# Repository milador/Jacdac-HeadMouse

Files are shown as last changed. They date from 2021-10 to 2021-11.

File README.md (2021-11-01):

# Jacdac-HeadMouse

A headmouse concept based on <a href="https://microsoft.github.io/jacdac-docs/">Jacdac</a> ecosystem. The sample <a href="https://makecode.microbit.org/_heFTpmWCwD0o">Jacdac-HeadMouse test code</a> was used during Microsoft Global Hackathon 2021.

## Main Unit

Top View: 
<p align="center">
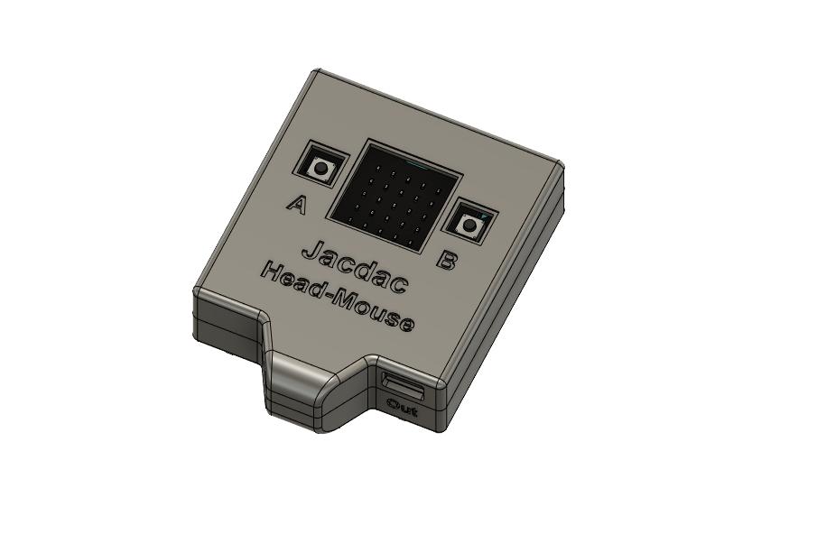
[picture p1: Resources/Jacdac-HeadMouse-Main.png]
Jacdac-HeadMouse Main Top View

</p>

Bottom View:  
<p align="center">
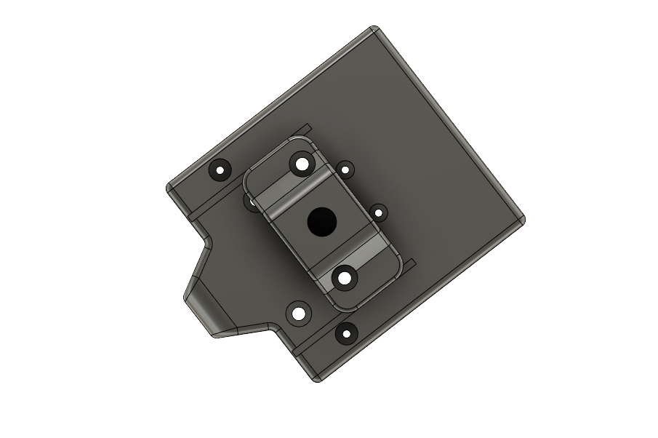
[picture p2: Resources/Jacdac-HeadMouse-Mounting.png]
Jacdac-HeadMouse Bottom View

</p>

Top Removed View:  
<p align="center">
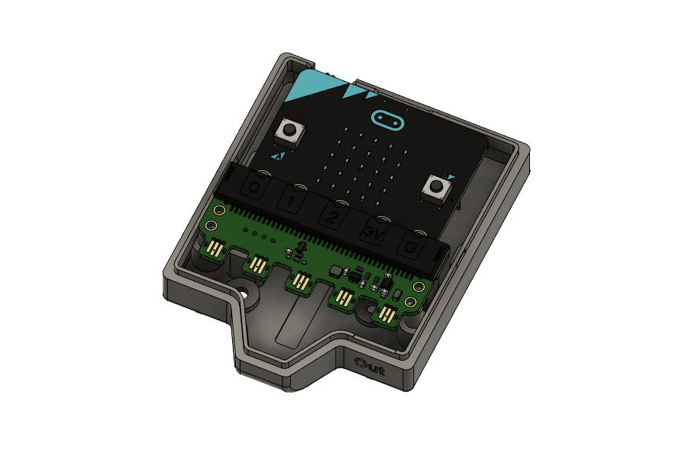
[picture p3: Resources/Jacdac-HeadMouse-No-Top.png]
Jacdac-HeadMouse Top Removed View

</p>

Accelerometer Inserted View:  
<p align="center">
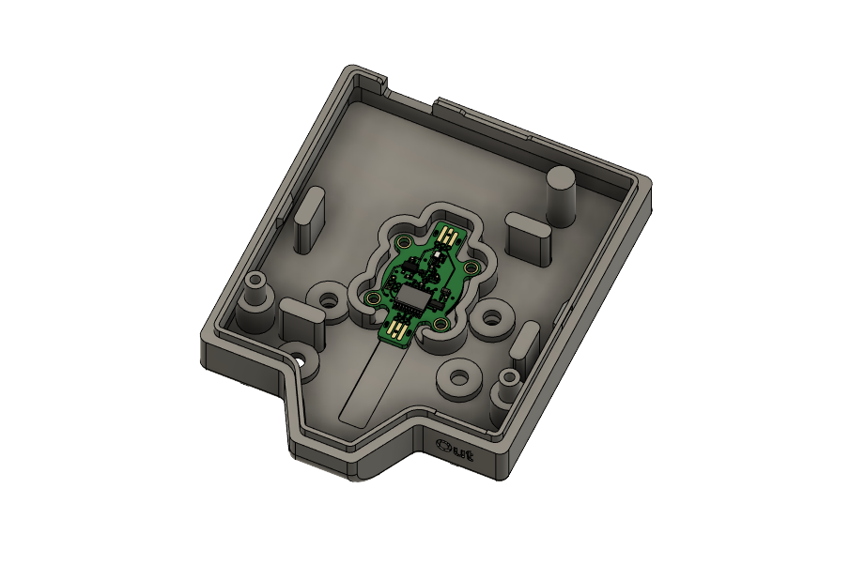
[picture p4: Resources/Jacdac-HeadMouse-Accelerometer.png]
Jacdac-HeadMouse Accelerometer Inserted View

</p>

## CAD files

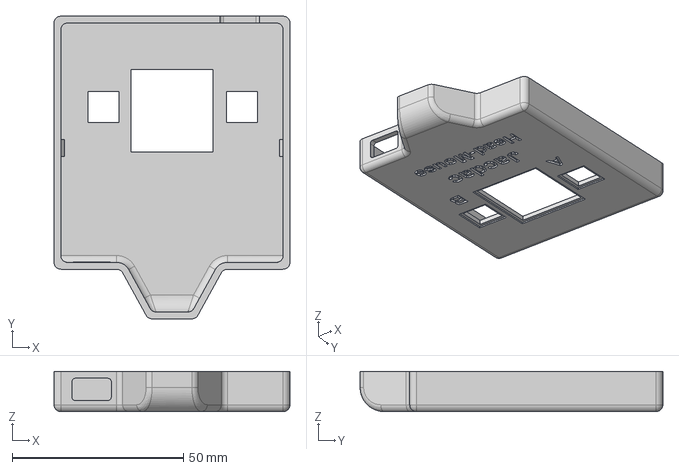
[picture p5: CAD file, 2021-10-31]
Hardware/Enclosure/STEP/Jacdac-HeadMouse-Top.step
69.0 x 88.5 x 11.8 mm

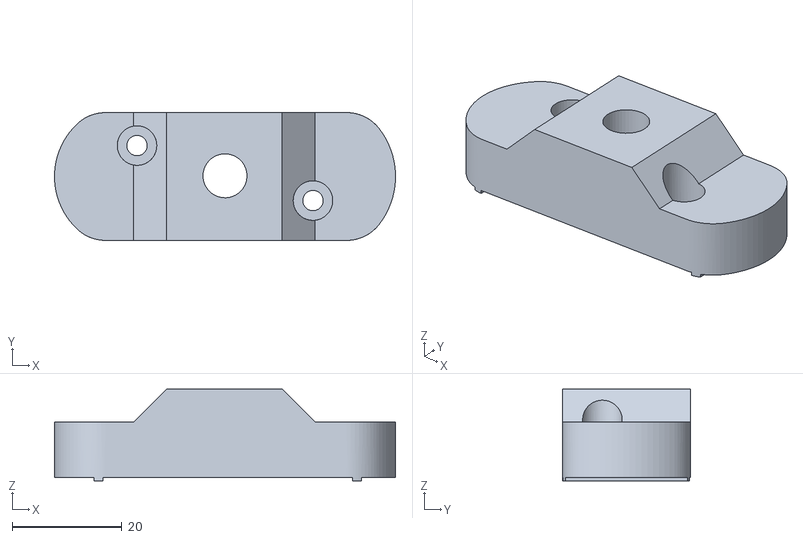
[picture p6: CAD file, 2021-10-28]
Hardware/Enclosure/STL/Jacdac-HeadMouse-Mounting-v1.stl
62.0 x 23.2 x 16.7

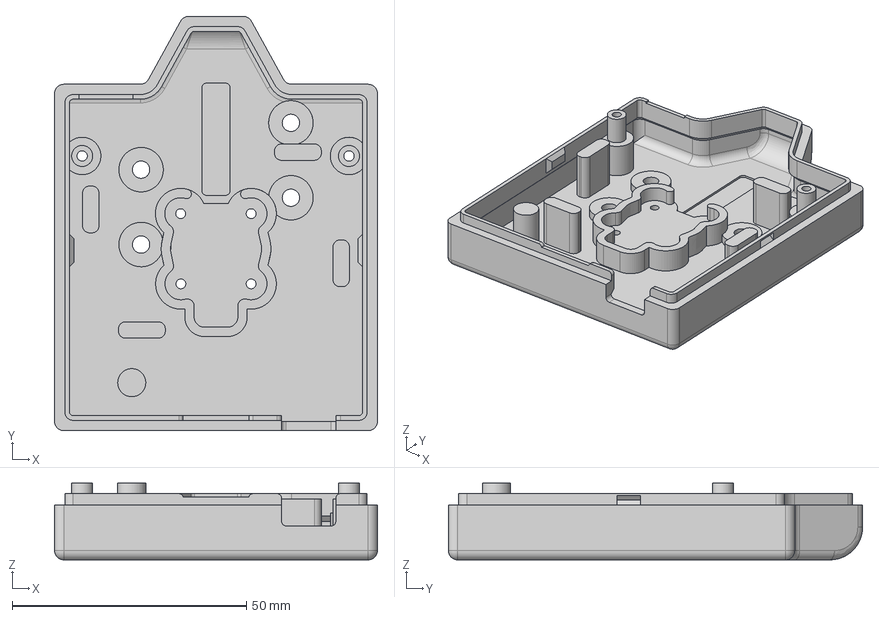
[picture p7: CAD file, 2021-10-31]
Hardware/Enclosure/STEP/Jacdac-HeadMouse-Bottom.step
69.0 x 88.5 x 16.4 mm

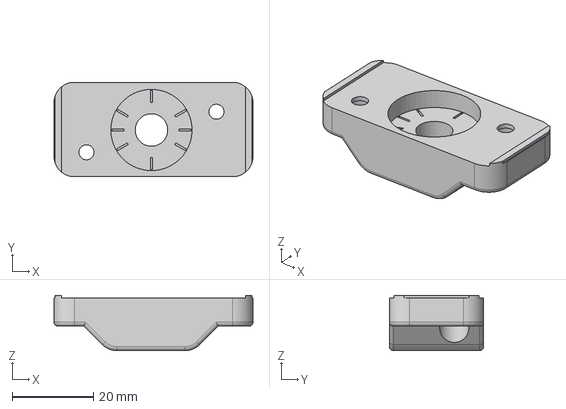
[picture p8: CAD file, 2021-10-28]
Hardware/Enclosure/STEP/Jacdac-HeadMouse-Mounting.step
49.0 x 23.2 x 13.6 mm

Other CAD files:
Hardware/Enclosure/STL/Jacdac-HeadMouse-Bottom.stl
Hardware/Enclosure/STL/Jacdac-HeadMouse-Mounting.stl
Hardware/Enclosure/STL/Jacdac-HeadMouse-Top.stl

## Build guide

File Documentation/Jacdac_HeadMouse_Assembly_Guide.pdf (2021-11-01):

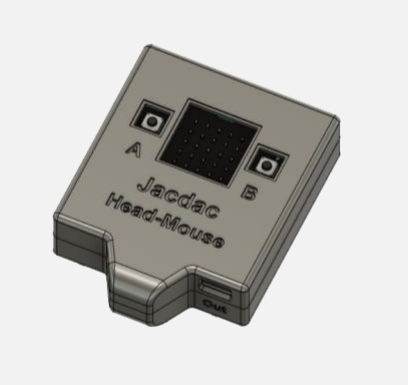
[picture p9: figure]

# JACDAC HEADMOUSE

A head mouse concept based on Jacdac microcontrollers ecosystem.

## Version 1.0

https://github.com/milador/Jacdac-HeadMouse

1

## Contents

Components List | 1
Software | 3
JavaScript Demo Code | 3
Hardware Assembly | 6
Enclosure design | 6
Assembly | 7

## Components List

### 1. MICRO:BIT V2 x 1

2. MICRO:BIT JACDAPTOR (https://microsoft.github.io/jacdac-docs/devices/microbit/foundation/microbitv2) x 1
3. JACDAC ACCELEROMETER MODULE (https://microsoft.github.io/jacdac-docs/devices/microsoft/research/jmaccelerometer30v10) x 1

### 4. JACDAC CABLE x 2

### 5. LITHIUM-ION POLYMER BATTERY- 3.7V 1200MAH (https://www.adafruit.com/product/258) x 1

### 6. M3 HEX NUT x 2

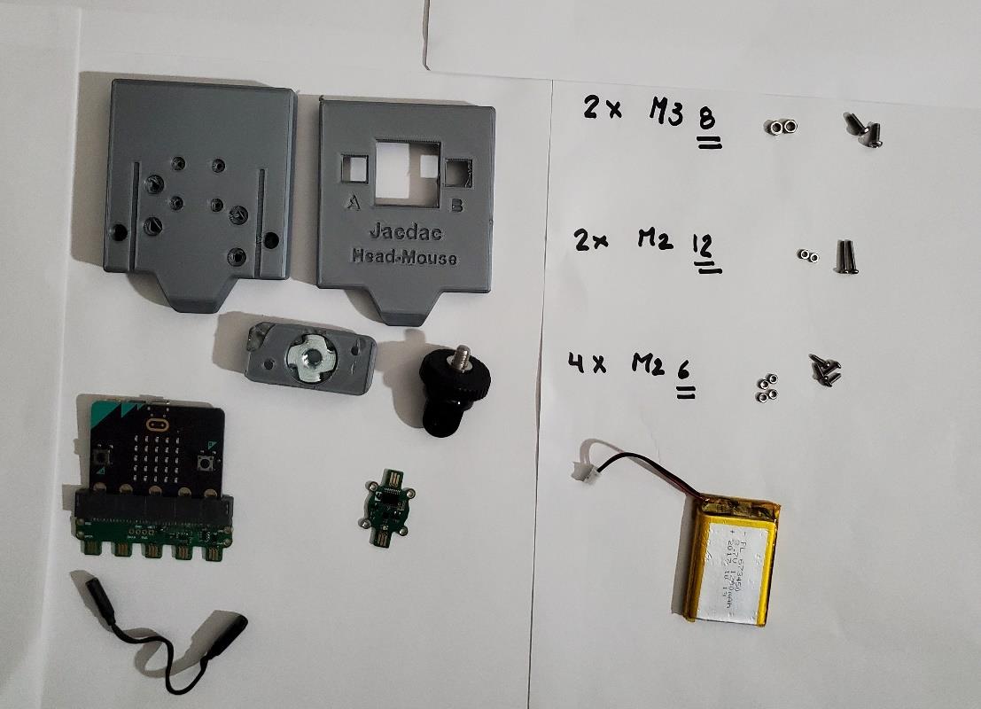
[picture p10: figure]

2

### 7. M3-8MM SCREW x 2

### 8. M2 HEX NUT x 6

### 9. M2-6MM SCREW x 4

### 10. M2-12MM SCREW x 2

11. AMAZON BASICS HEAD STRAP CAMERA MOUNT FOR GOPRO (https://www.amazon.ca/gp/product/B00R4YCKIK/) x 1
12. GOPRO MOUNT TO 1/4-INCH 20 CAMERA ADAPTER (https://www.amazon.ca/gp/product/B00IQ7PRHU) x 1
13. 1/4-INCH 20 TEE NUT x 1
14. (OPTIONAL) JACDAC ACCESS SWITCH OUTPUT MODULE (https://microsoft.github.io/jacdac-docs/devices/microsoft/research/jmaccessswitchoutputv11) x 1
- Item 14 is optional, and it’s only required if you would like to control an access switch instead of

cursor.

3

## Software

The demo code written using MakeCode blocks is available and it can be accessed through following link.

https://makecode.microbit.org/_heFTpmWCwD0o

### JavaScript Demo Code

You can also copy and paste the following code to MakeCode JavaScript code editor field:

input.onButtonPressed(Button.A, function () {

initialize()

})

function initialize () {

counter = 3

while (counter >= 0) {

basic.showNumber(counter)

basic.pause(1000)

counter += -1

}

basic.pause(200)

soundExpression.hello.play()

x_init = modules.accelerometer1.x()

y_init = modules.accelerometer1.z()

}

let y_val = 0

let x_val = 0

let counter = 0

4

let y_init = 0

let x_init = 0

let count = 0

let x_threshold = 0.05

let y_up_threshold = 0.22

let y_down_threshold = 0.05

x_init = -0.2

y_init = 0.1

initialize()

basic.forever(function () {

led.stopAnimation()

if (modules.accelerometer1.x() < x_init - x_threshold) {

x_val = 1

} else if (modules.accelerometer1.x() > x_init + x_threshold) {

x_val = -1

} else {

x_val = 0

}

if (modules.accelerometer1.z() < y_init - y_up_threshold) {

y_val = 1

} else if (modules.accelerometer1.z() > y_init + y_down_threshold) {

y_val = -1

} else {

y_val = 0

}

if (x_val == 0 && y_val == 0) {

basic.showLeds(`

5

`)

modules.hidKeyboard1.clear()

} else if (x_val == 0 && y_val != 0) {

if (y_val > 0) {

basic.showArrow(ArrowNames.North)

modules.hidKeyboard1.key(jacdac.HidKeyboardAction.Press, jacdac.HidKeyboardModifiers.None, jacdac.HidKeyboardKey.UpArrow)

} else {

basic.showArrow(ArrowNames.South)

modules.hidKeyboard1.key(jacdac.HidKeyboardAction.Press, jacdac.HidKeyboardModifiers.None, jacdac.HidKeyboardKey.DownArrow)

}

} else if (x_val != 0 && y_val == 0) {

if (x_val > 0) {

basic.showArrow(ArrowNames.East)

modules.hidKeyboard1.key(jacdac.HidKeyboardAction.Press, jacdac.HidKeyboardModifiers.None, jacdac.HidKeyboardKey.LeftArrow)

} else {

basic.showArrow(ArrowNames.West)

modules.hidKeyboard1.key(jacdac.HidKeyboardAction.Press, jacdac.HidKeyboardModifiers.None, jacdac.HidKeyboardKey.RightArrow)

}

} else if (x_val != 0 && y_val != 0) {

if (x_val > 0 && y_val > 0) {

basic.showArrow(ArrowNames.NorthEast)

} else if (x_val < 0 && y_val > 0) {

basic.showArrow(ArrowNames.NorthWest)

} else if (x_val < 0 && y_val < 0) {

basic.showArrow(ArrowNames.SouthWest)

} else if (x_val < 0 && y_val > 0) {

basic.showArrow(ArrowNames.SouthEast)

6

} else {

}

} else {

}

})

## Hardware Assembly

### Enclosure design

The enclosure/housing files in STL format can be downloaded from GitHub repository under Hardware directory.

https://github.com/milador/Jacdac-HeadMouse/tree/main/Hardware/Enclosure/STL

Please print the following STL files:

- Jacdac-HeadMouse-Top.stl x 1
- Jacdac-HeadMouse-Bottom.stl x 1
- Jacdac-HeadMouse-Mounting.stl x 1

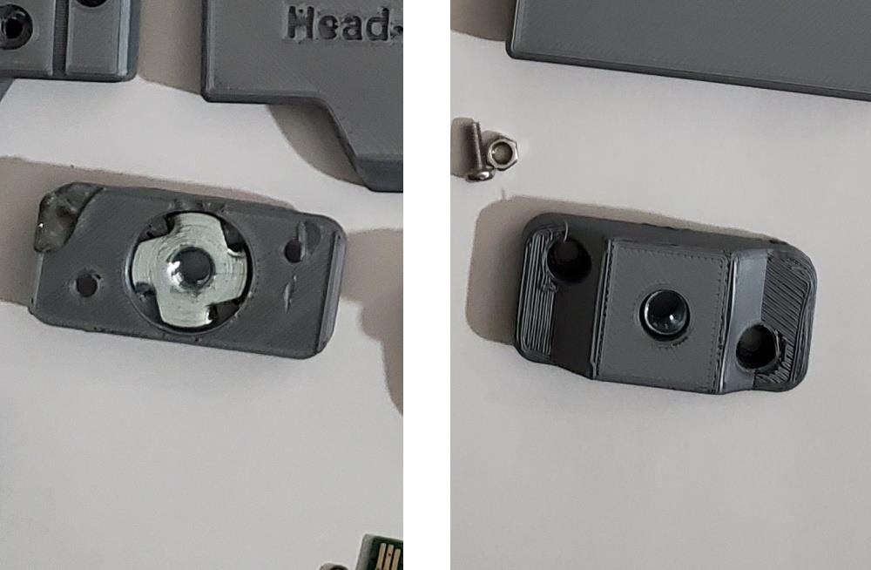
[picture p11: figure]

7

### Assembly

Step 1: Insert the 1/4-inch-20 Tee Nut into the mounting enclosure piece and press it inward using a soldering iron.

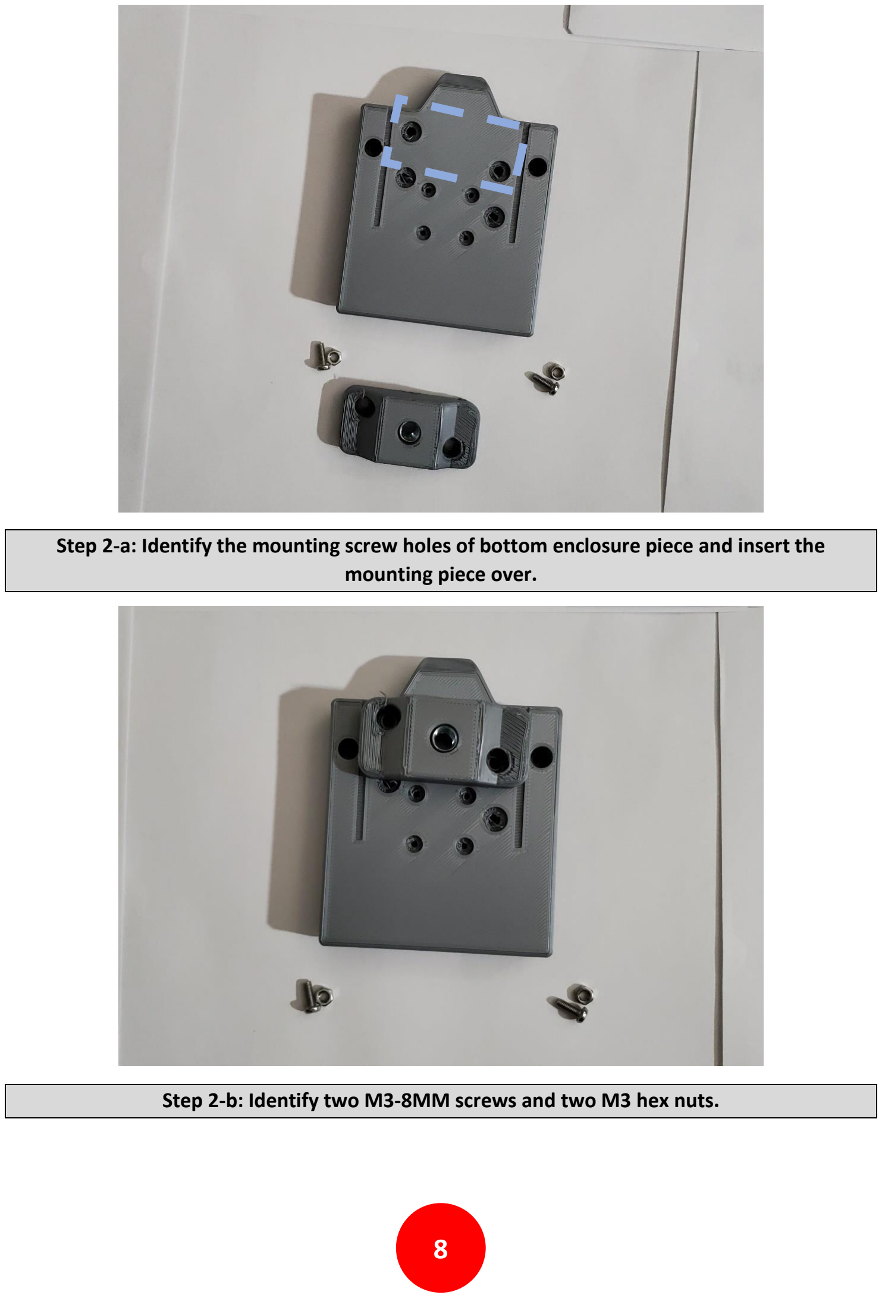
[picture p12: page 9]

8

Step 2-a: Identify the mounting screw holes of bottom enclosure piece and insert the mounting piece over.
Step 2-b: Identify two M3-8MM screws and two M3 hex nuts.

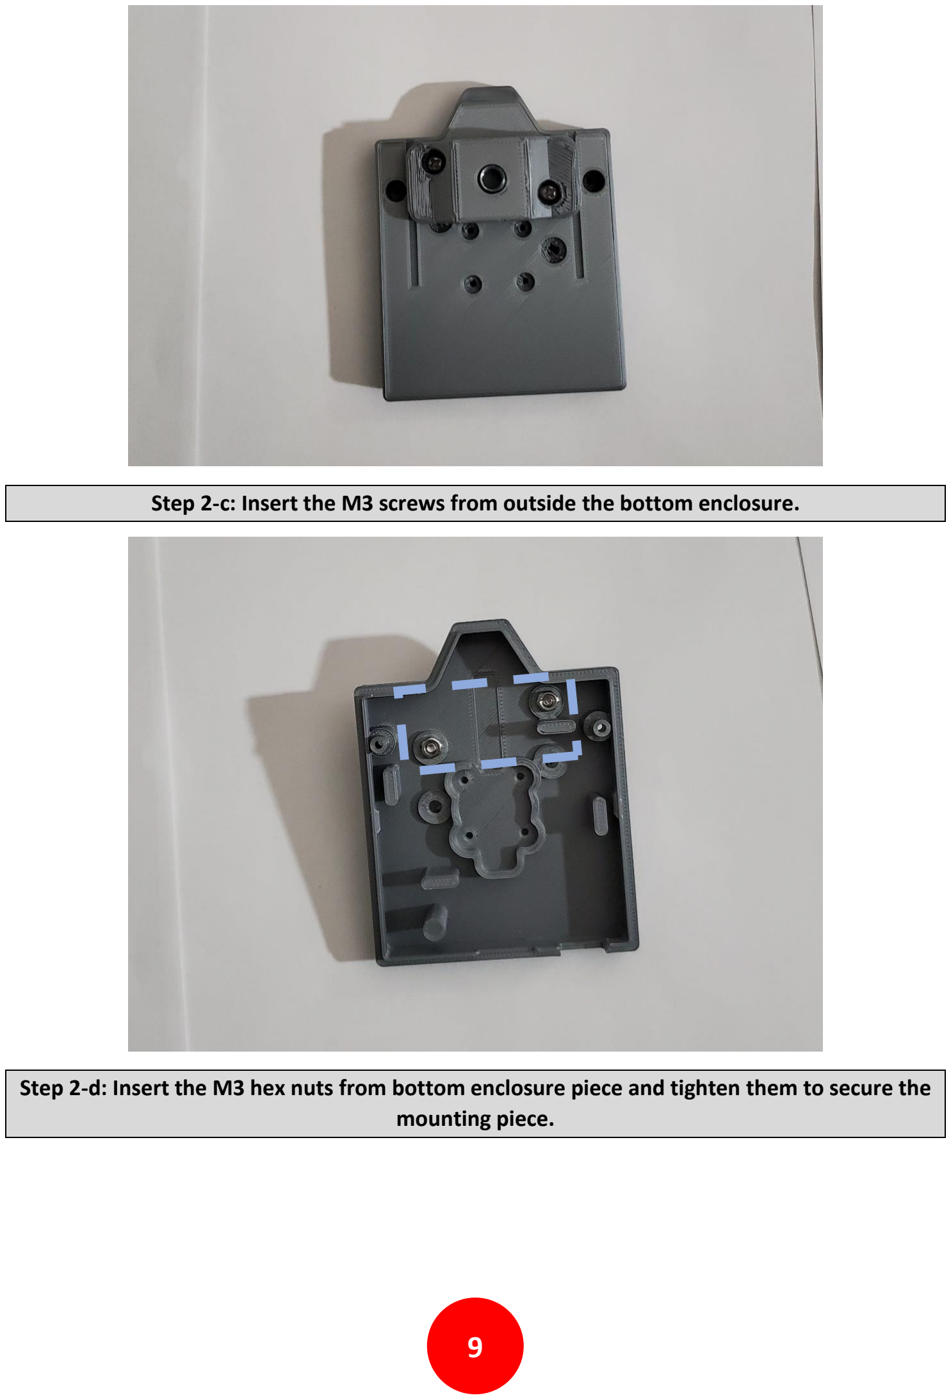
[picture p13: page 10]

9

Step 2-c: Insert the M3 screws from outside the bottom enclosure.
Step 2-d: Insert the M3 hex nuts from bottom enclosure piece and tighten them to secure the mounting piece.

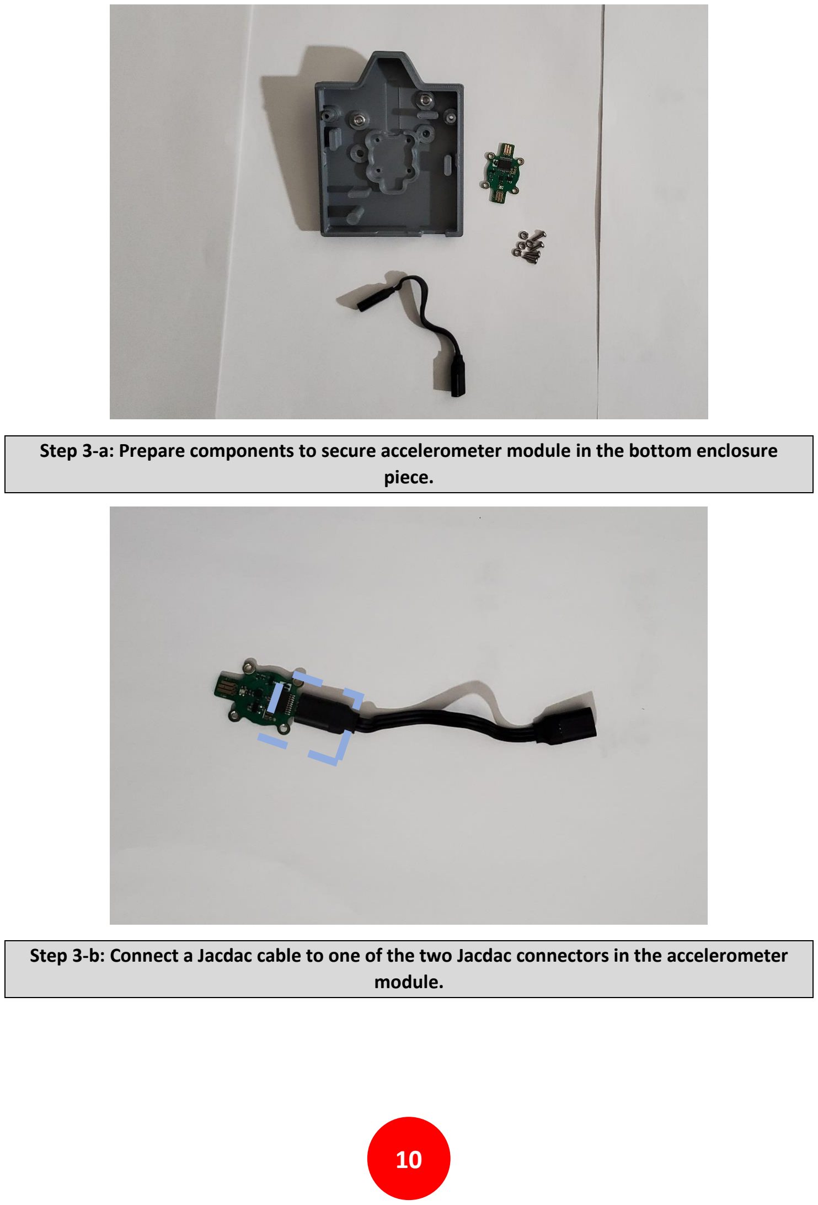
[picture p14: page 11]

10

Step 3-a: Prepare components to secure accelerometer module in the bottom enclosure piece.
Step 3-b: Connect a Jacdac cable to one of the two Jacdac connectors in the accelerometer module.

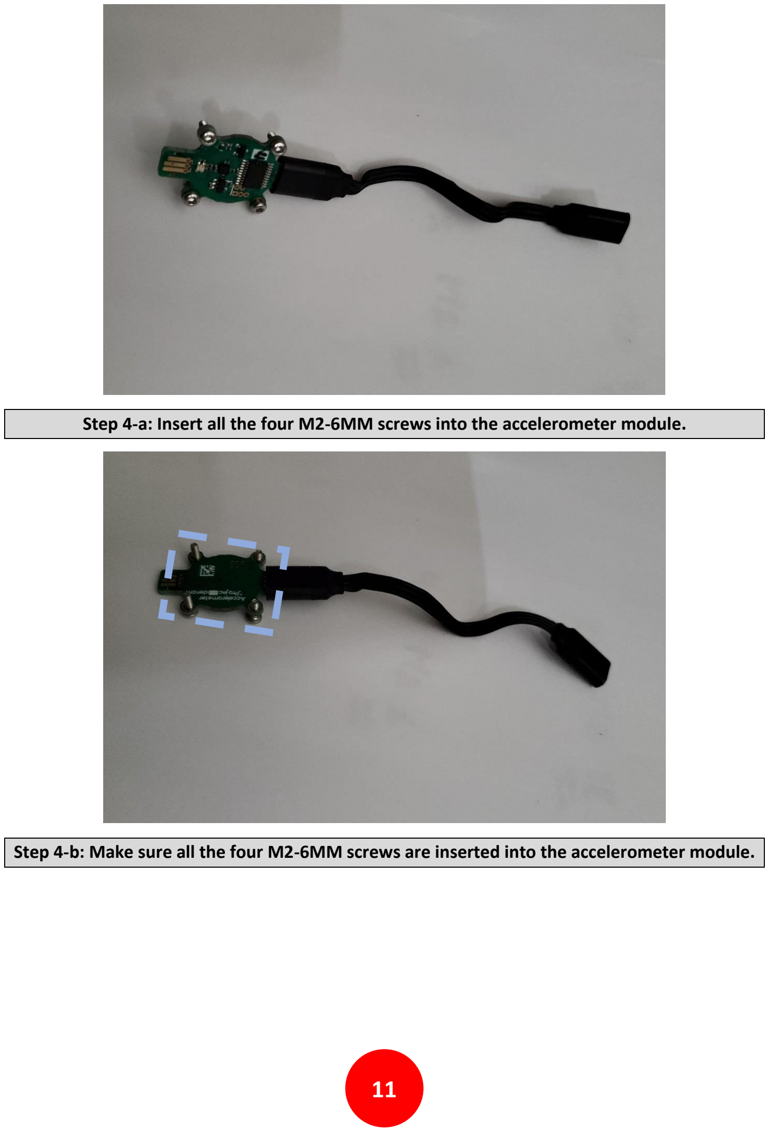
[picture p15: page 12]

11

Step 4-a: Insert all the four M2-6MM screws into the accelerometer module.
Step 4-b: Make sure all the four M2-6MM screws are inserted into the accelerometer module.

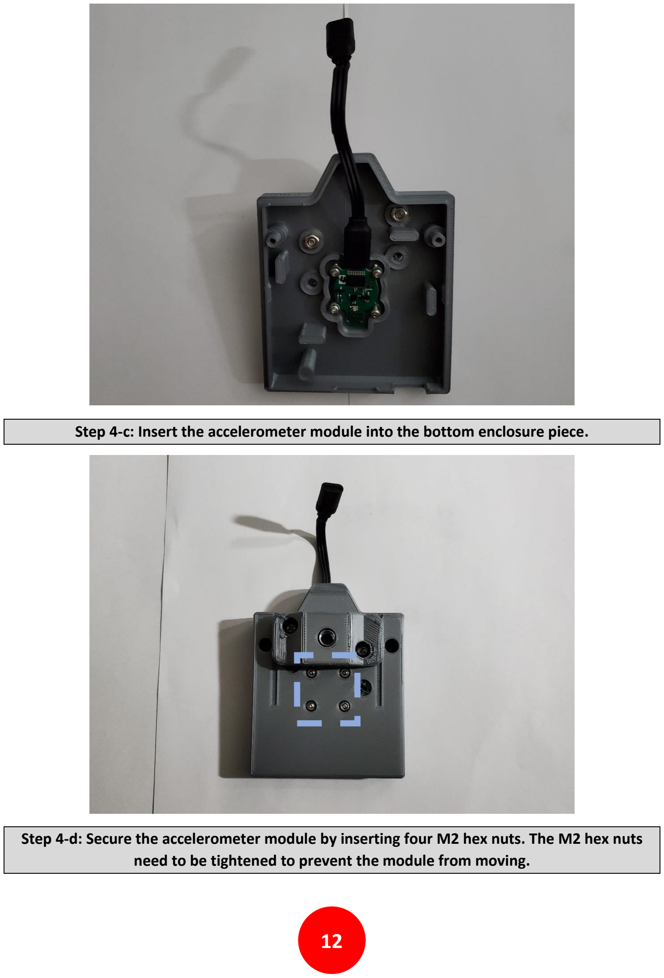
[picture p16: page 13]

12

Step 4-c: Insert the accelerometer module into the bottom enclosure piece.
Step 4-d: Secure the accelerometer module by inserting four M2 hex nuts. The M2 hex nuts need to be tightened to prevent the module from moving.

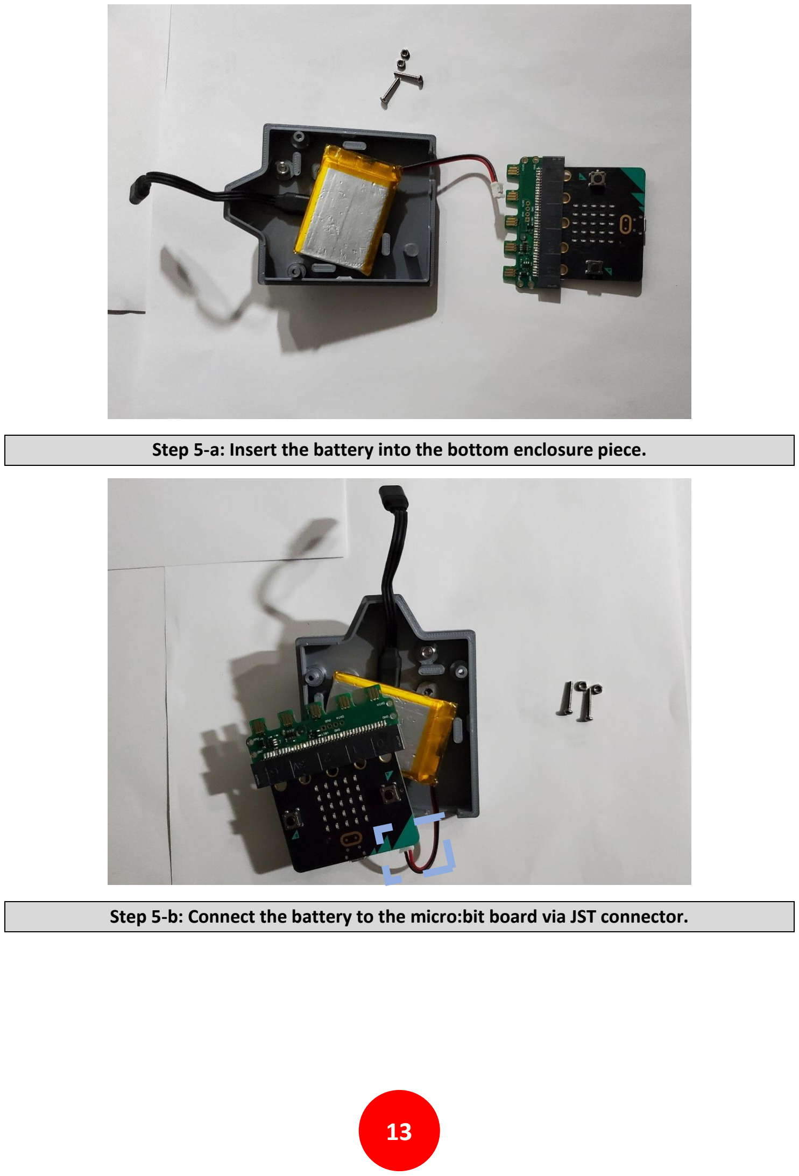
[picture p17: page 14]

13

Step 5-a: Insert the battery into the bottom enclosure piece.
Step 5-b: Connect the battery to the micro:bit board via JST connector.

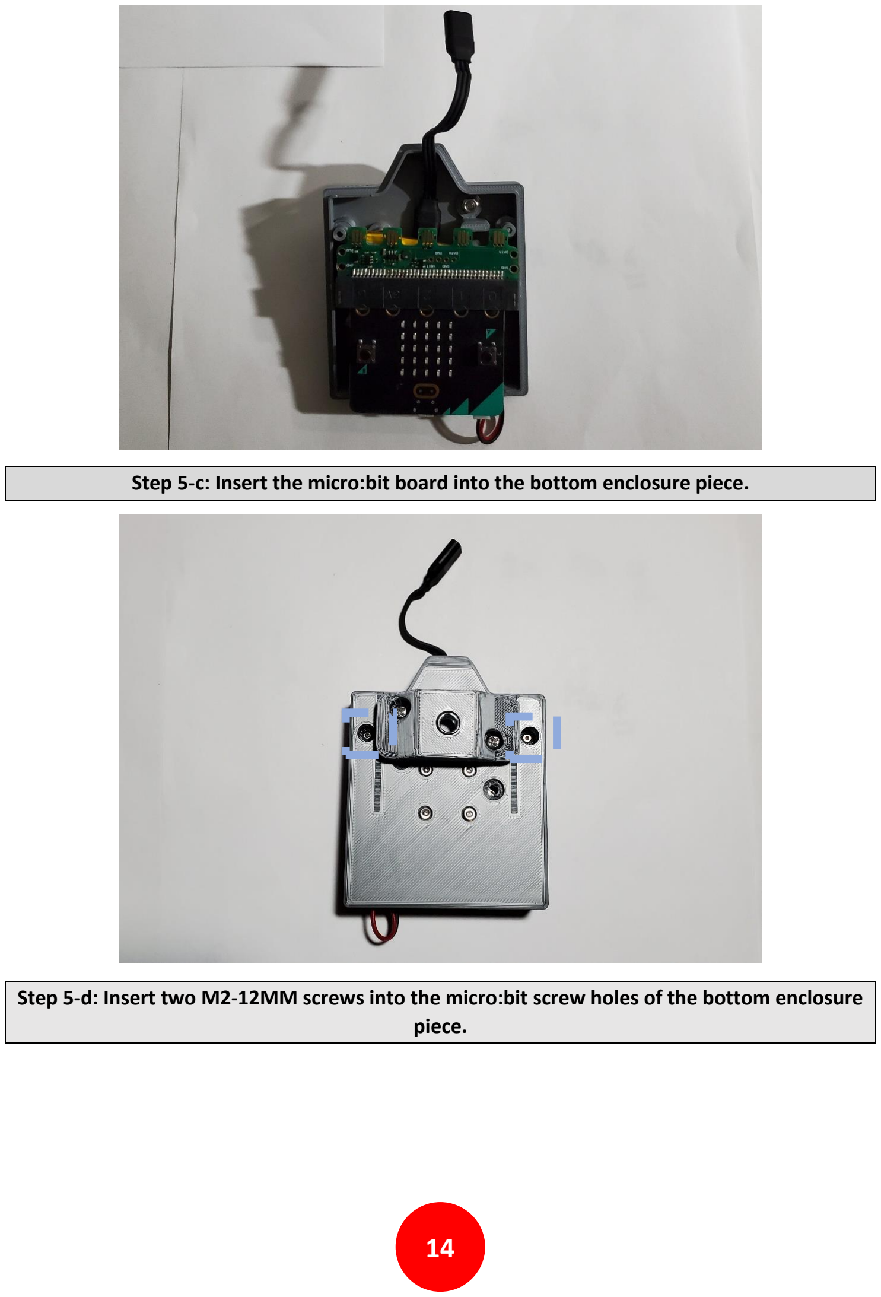
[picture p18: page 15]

14

Step 5-c: Insert the micro:bit board into the bottom enclosure piece.
Step 5-d: Insert two M2-12MM screws into the micro:bit screw holes of the bottom enclosure piece.

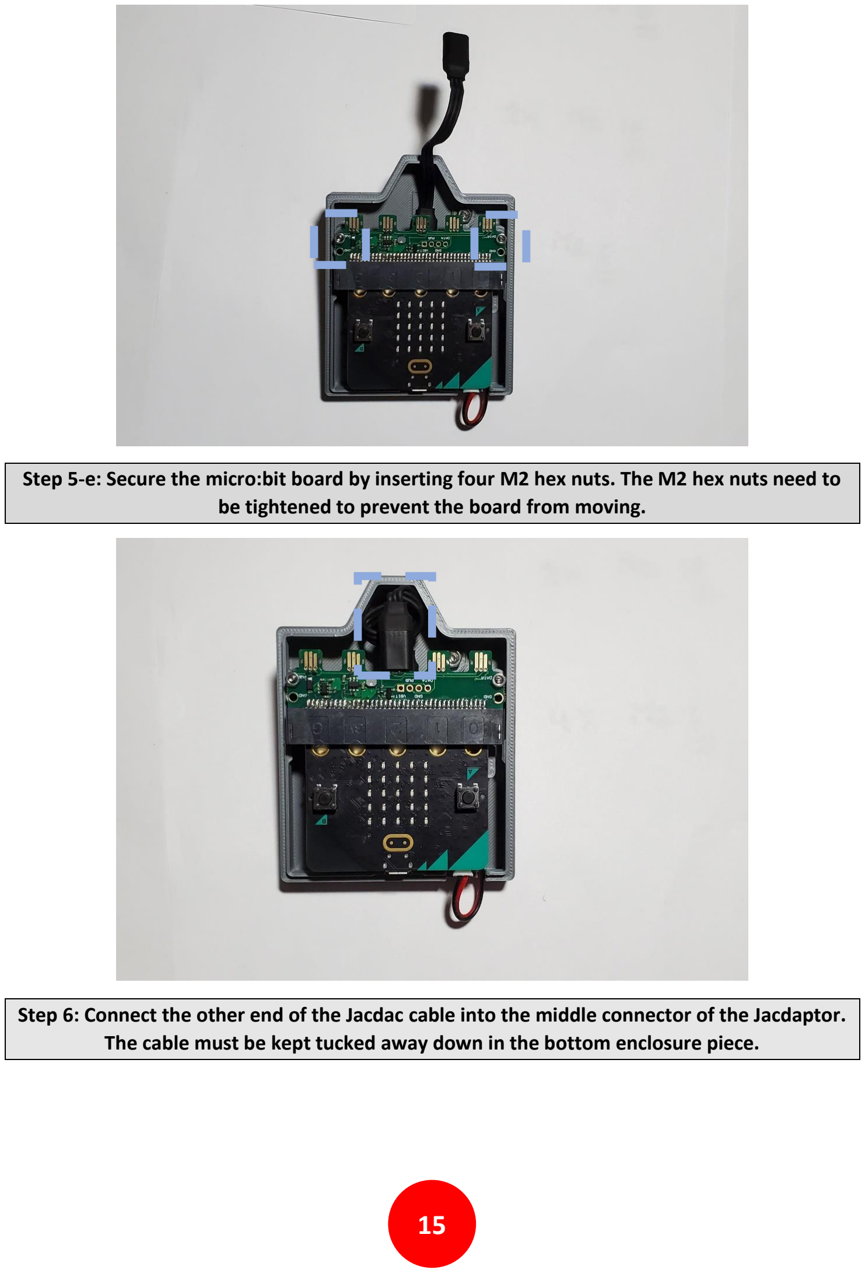
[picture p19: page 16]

15

Step 5-e: Secure the micro:bit board by inserting four M2 hex nuts. The M2 hex nuts need to be tightened to prevent the board from moving.
Step 6: Connect the other end of the Jacdac cable into the middle connector of the Jacdaptor. The cable must be kept tucked away down in the bottom enclosure piece.

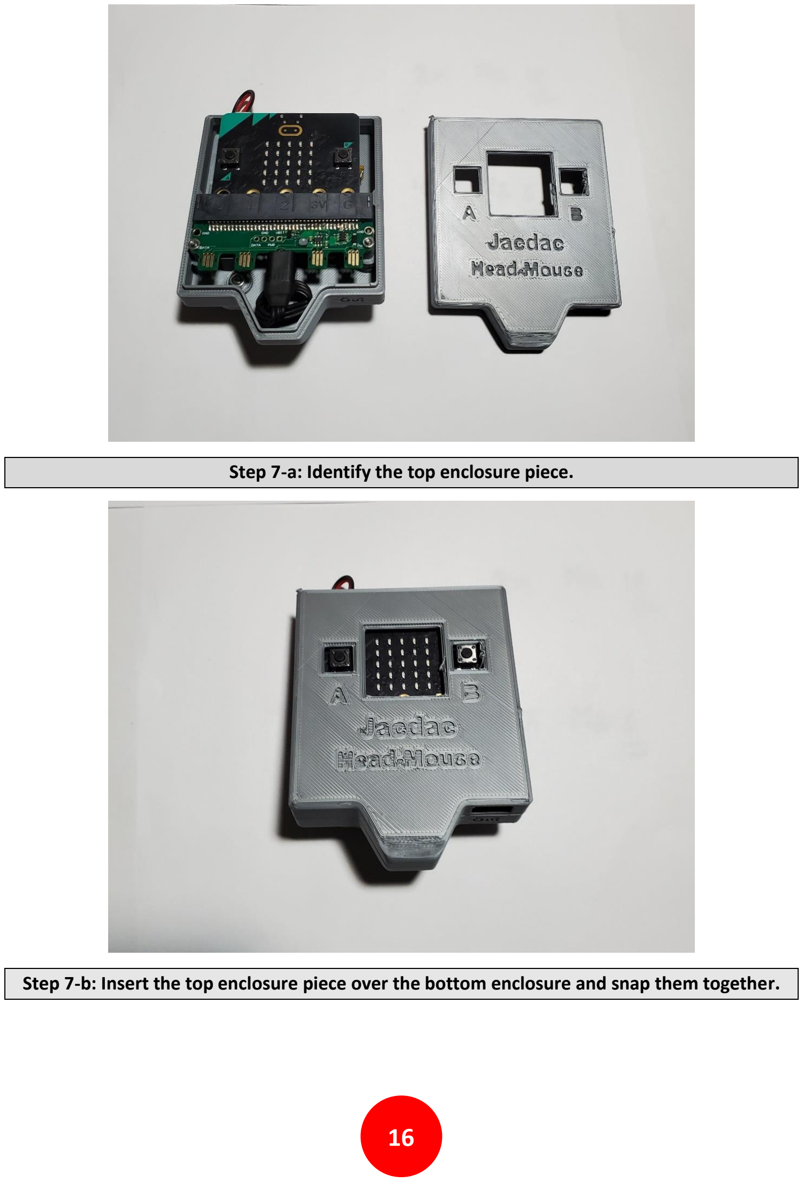
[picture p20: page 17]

16

Step 7-a: Identify the top enclosure piece.
Step 7-b: Insert the top enclosure piece over the bottom enclosure and snap them together.

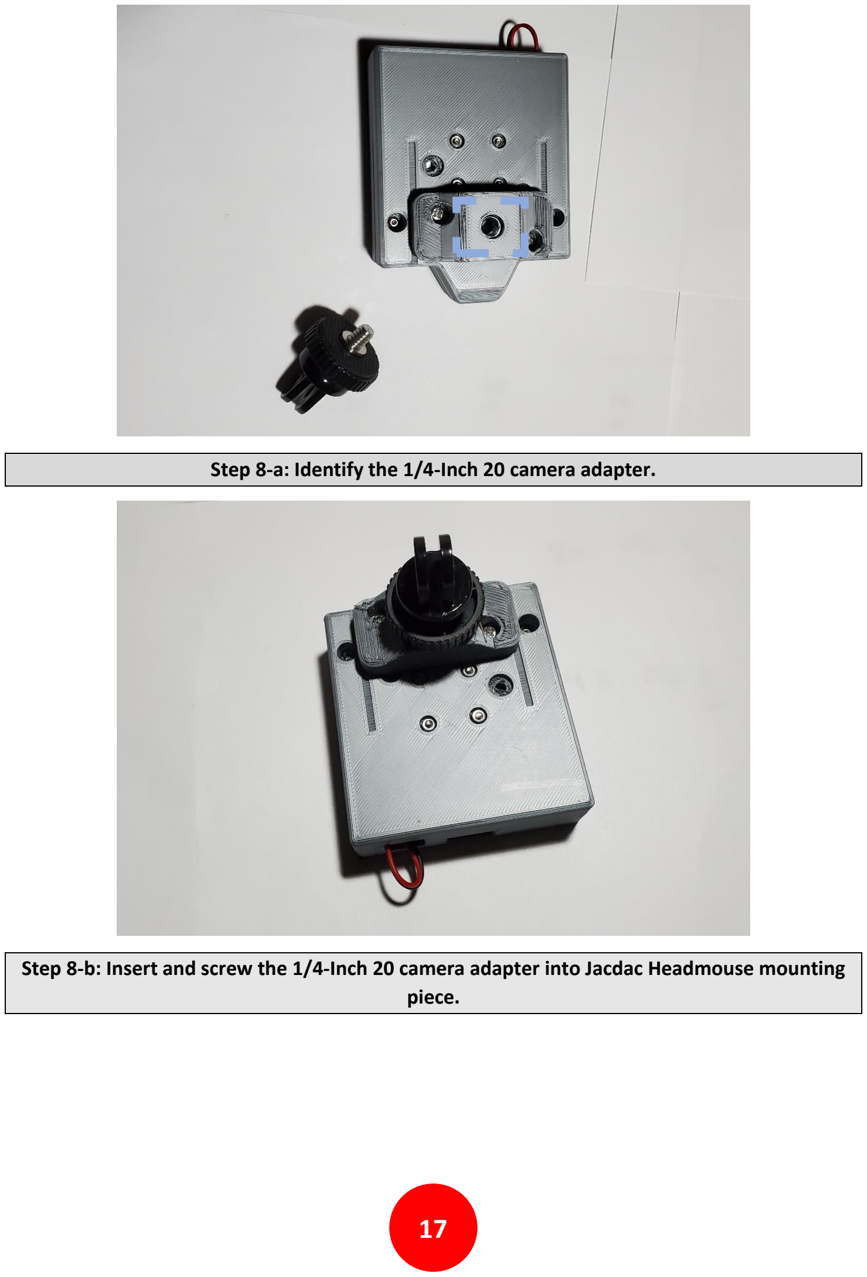
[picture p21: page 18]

17

Step 8-a: Identify the 1/4-Inch 20 camera adapter.
Step 8-b: Insert and screw the 1/4-Inch 20 camera adapter into Jacdac Headmouse mounting piece.

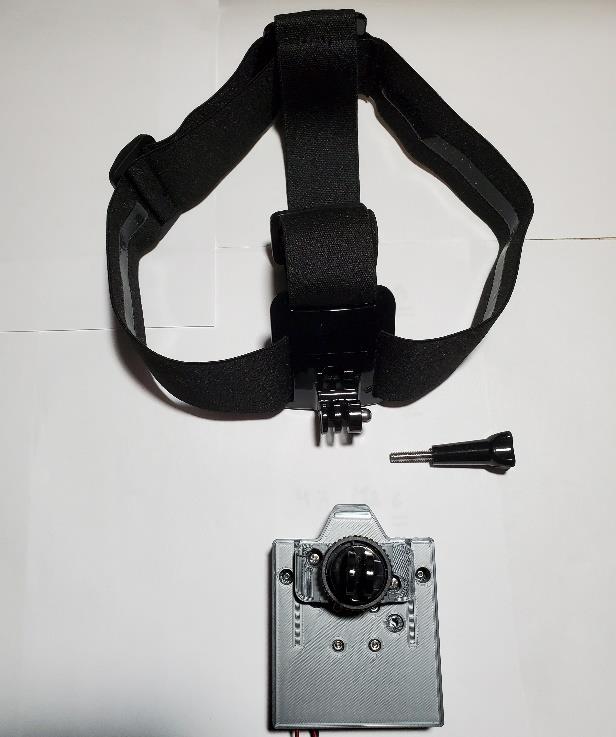
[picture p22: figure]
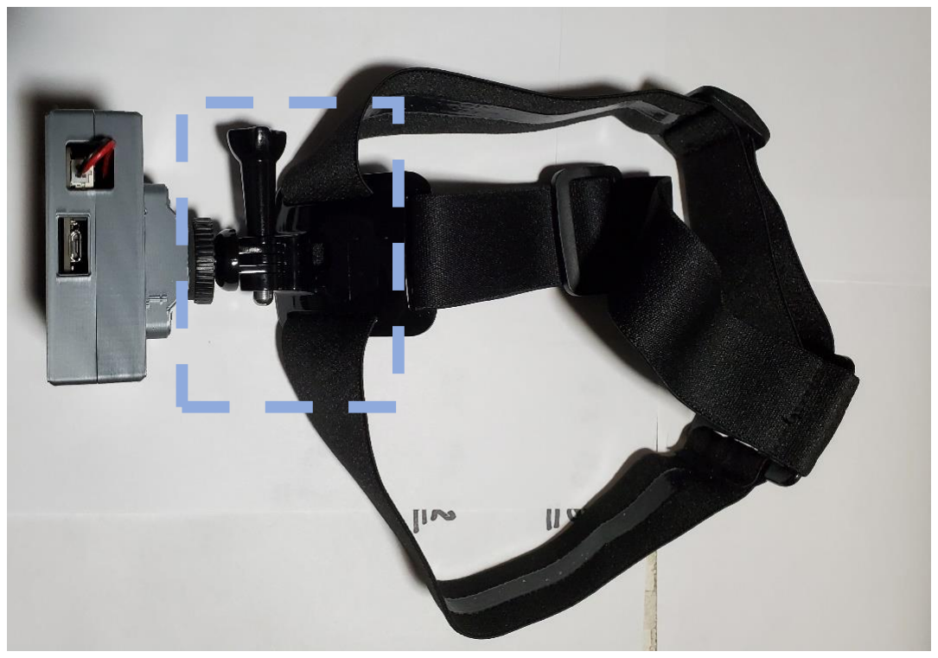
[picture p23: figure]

18

Step 8-c: Identify the head strap camera mount.
Step 8-d: Connect the head strap camera mount to the Jacdac HeadMouse enclosure.

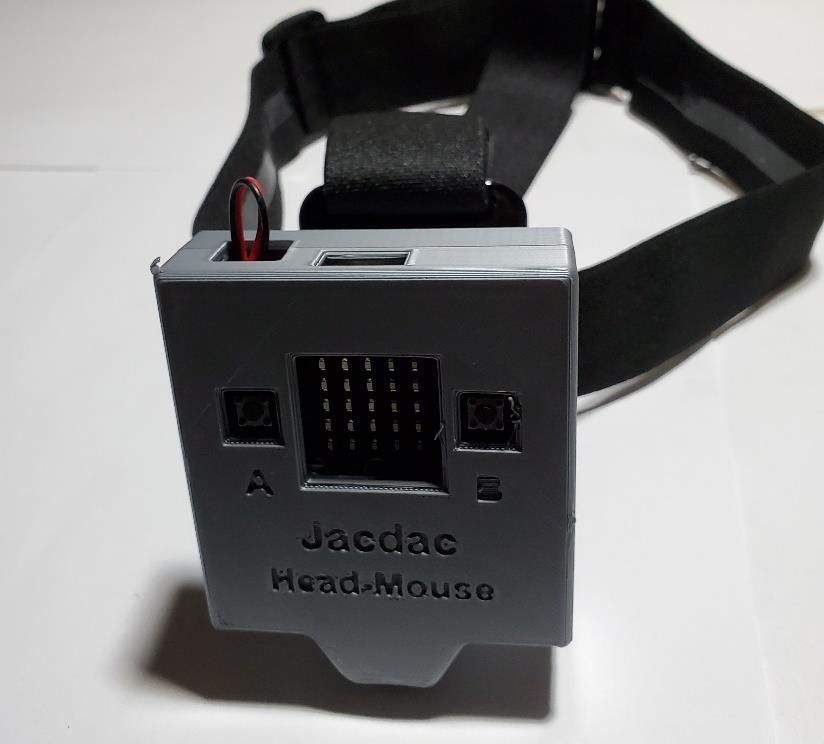
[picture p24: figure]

19

Step 9: The Jacdac HeadMouse is now fully assembled.

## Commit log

2021-10-31 Updated stl files
    [Jacdac-HeadMouse-Bottom.step, Jacdac-HeadMouse-Bottom.stl, Jacdac-HeadMouse-Top.step, Jacdac-HeadMouse-Top.stl]
2021-11-01 Added Assembly Guide
